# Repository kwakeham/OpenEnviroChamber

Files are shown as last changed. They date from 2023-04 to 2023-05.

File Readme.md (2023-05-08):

# Parts
- Arduino Leonardo (Uno or similar should work)
- Heater Power Fet: PSMN1R1-30PL (1.3mohm) or similar
- Fan Power Fet: P16NF06L or similar
- Heatsinks: Ohmite EV-T220-38E This mounts
- 2x XT60 connector pairs
- 2x "JST" 2 pin (I know JST is a brand but that's how they come up on Aliexpress or Jungle site)
- Adafruit MAX31855 Breadout Board (or similar but the mount won't line up)
- 2 x Bar magnets that fit in a 59 x 10mm trench (I think they were imperial)

- Top and Enclosure 3d printed
- M3 Inserts for the arduino mount
- 2 x 2mm self tapping screws for the MAX31855
- 12v Powersupply (min 5 amps)
- 50W PTC heater with fan (Jungle site)
- SSR for the compressor

- Thick Silicone wire for the 12v, enough to handle 5A but more for safety

# schematic
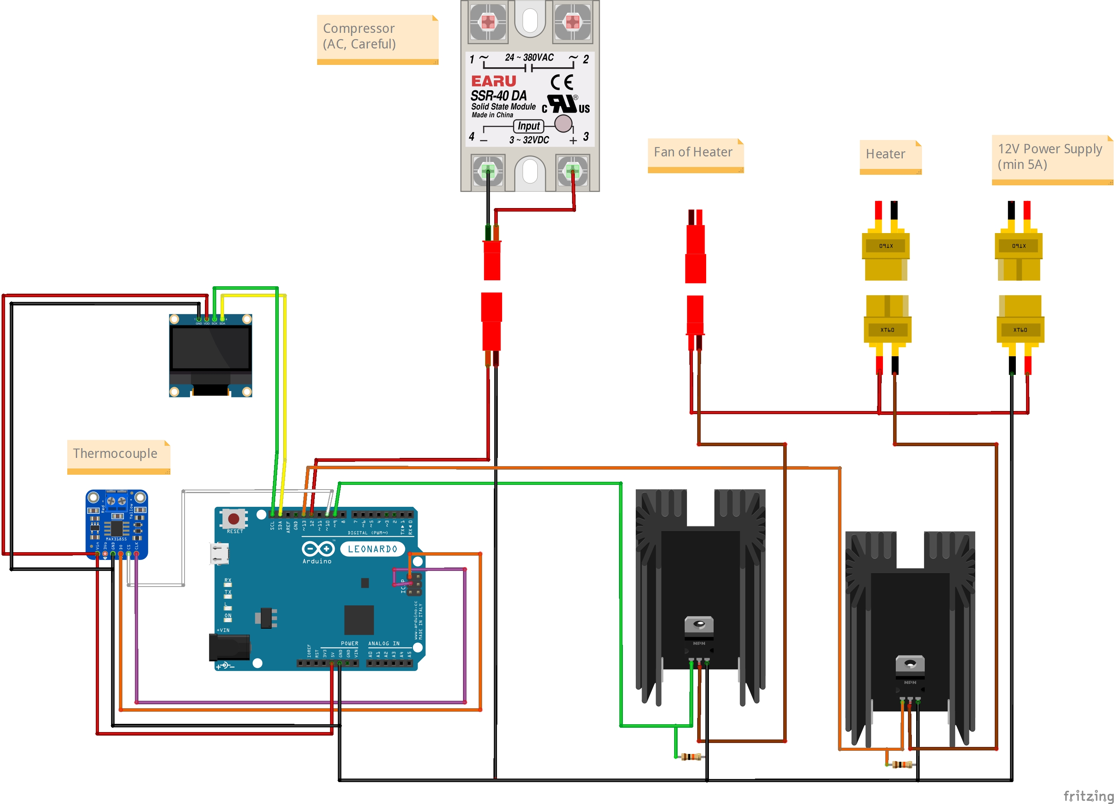
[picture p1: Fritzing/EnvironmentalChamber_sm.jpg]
Image of schematic


# Notes
I soldered wires to the back of the Arduino and modules because the push wires tend to be unreliable. I can't have a device that uses high power 12v and 120v AC going on the fritz. I suggest you do the same. Means debuging is easier

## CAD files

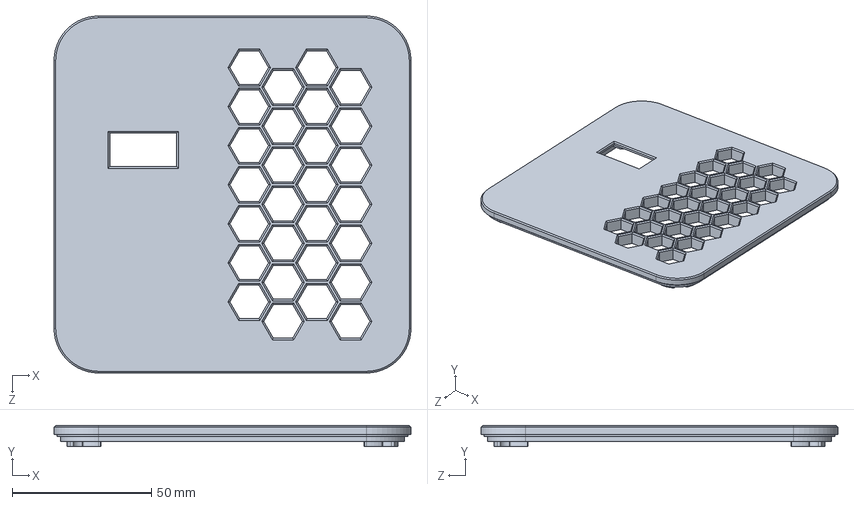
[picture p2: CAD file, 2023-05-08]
enclosure/Top.STEP
128.0 x 7.60 x 128.0 mm

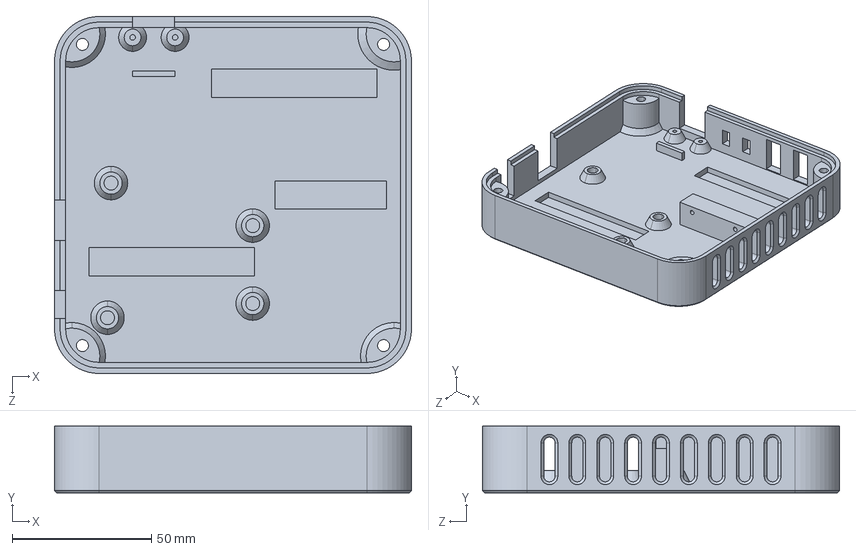
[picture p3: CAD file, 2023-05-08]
enclosure/Enclosure.STEP
128.0 x 24.0 x 128.0 mm

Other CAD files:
enclosure/Enclosure.3MF
enclosure/Top.3MF

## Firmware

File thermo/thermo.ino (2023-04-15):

/*
Frigidbear
*/

#include <SPI.h>
#include "Adafruit_MAX31855.h"
#include <Wire.h>
#include "SSD1306Ascii.h"
#include "SSD1306AsciiWire.h"
#include "ArduPID.h"
#include "Vrekrer_scpi_parser.h"

#define compressor_rest_time 300000 //5 minutes
#define cool_loop_time 30000 //30 seconds, we want the cooling loop time to be slower because compressors respond slowly

#define compressor_pin 12
#define heater_pin 13
#define fan_pin 9

// #define SCREEN_WIDTH 128 // OLED display width, in pixels
// #define SCREEN_HEIGHT 64 // OLED display height, in pixels
// // Declaration for an SSD1306 display connected to I2C (SDA, SCL pins)
// #define OLED_RESET     4 // Reset pin # (or -1 if sharing Arduino reset pin)
// Adafruit_SSD1306 display(SCREEN_WIDTH, SCREEN_HEIGHT, &Wire, OLED_RESET);

// 0X3C+SA0 - 0x3C or 0x3D
#define I2C_ADDRESS 0x3C
// Define proper RST_PIN if required.
#define RST_PIN -1
SSD1306AsciiWire oled;

#define MAXCS   10
Adafruit_MAX31855 thermocouple(MAXCS);

enum chamber_state_t {
  unknown_state,
  idle_state,
  cooling_state,
  heating_state
};

bool system_running = false;
bool compressor_state = false;
chamber_state_t chamber_state = idle_state;
double chamber_temp;
unsigned long compressor_stop_time = 0;

//ardupid
double heat_output;
double cool_output;
// Arbitrary setpoint and gains - adjust these as fit for your project:
double setpoint = 0;
double p_h = 30;
double i_h = 0.0002; //much lower I term
double d_h = 0;

double p_c = 11; //1 degree (gain of 10) should be good, but rounding and such so 11 it is
double i_c = 0.0002; //some i term for cooling
double d_c = 0;

//two controllers because we might end up tuning differently
ArduPID heatController;
ArduPID coolController;

SCPI_Parser my_instrument;

void setup() {

  Serial.begin(115200);
  while (!Serial) delay(1); // wait for Serial on Leonardo/Zero, etc

  Wire.begin();
  Wire.setClock(400000L);

#if RST_PIN >= 0
  oled.begin(&Adafruit128x64, I2C_ADDRESS, RST_PIN);
#else // RST_PIN >= 0
  oled.begin(&Adafruit128x64, I2C_ADDRESS);
#endif // RST_PIN >= 0

  oled.setFont(Adafruit5x7);
  oled.clear();

  //ensure the MAX31855 responds
  Serial.println("MAX31855 test");
  delay(200);  // wait for MAX chip to stabilize

  Serial.print("Initializing sensor...");
  if (!thermocouple.begin()) {
    Serial.println("ERROR.");
    while (1) delay(10);
  }
  Serial.println("MAX31855 startup DONE.");

  //set the SSR and Mosfet pin output
  pinMode(compressor_pin, OUTPUT);
  pinMode(heater_pin, OUTPUT);
  pinMode(fan_pin, OUTPUT);
  digitalWrite(fan_pin, true); //fan always on for now
  compressor_run(0); //This should be okay as it shouldn't update the compressor_state (initialize to false) and therefore compressor_stop_time should still be 0 for edge case on statup
  heater_control(0);

  //setup the two controllers.
  heatController.begin(&chamber_temp, &heat_output, &setpoint, p_h, i_h, d_h);
  heatController.setOutputLimits(0, 255);
  heatController.setWindUpLimits(0, 100); // Growth bounds for the integral term to prevent integral wind-up
  heatController.stop();                // Turn off the PID controller (compute() will not do anything until start() is called)
    
  coolController.begin(&chamber_temp, &cool_output, &setpoint, p_c, i_c, d_c);
  coolController.setOutputLimits(-255, 100); //allow some heat, but not much because we won't update quickly and don't want to fight compressor with heater
  coolController.setWindUpLimits(-20, 0); // limit cooling antiwindup but no heating integral
  coolController.setSampleTime(cool_loop_time);      // Slow time, but not too slow, compressor protection code should ensure no damage to compressor

  //scpi setup
  statusupdate("Waiting", system_running);
  oled.setCursor(0,1);
  oled.print("Stopped");

  my_instrument.RegisterCommand(F("*IDN?"), &Identify);
  my_instrument.SetCommandTreeBase(F("ENVI"));
    my_instrument.RegisterCommand(F(":SETTemperature"), &SetTemperature);
    my_instrument.RegisterCommand(F(":GETSettemperature?"), &GetSetTemperature);
    my_instrument.RegisterCommand(F(":TEMPerature?"), &GetTemperature);
    my_instrument.RegisterCommand(F(":COOL"), &ChamberMode);
    my_instrument.RegisterCommand(F(":HEAT"), &ChamberMode);
    my_instrument.RegisterCommand(F(":STAT?"), &ChamberState);
    my_instrument.RegisterCommand(F(":RUN"), &ChamberRun);
    my_instrument.RegisterCommand(F(":RUN?"), &isChamberRun);
    my_instrument.RegisterCommand(F(":STOP"), &ChamberStop);
    
  my_instrument.PrintDebugInfo(Serial);
}


void loop(void) {
  readtemp();
  my_instrument.ProcessInput(Serial, "\n");
  temperature_control();
  // display.display();
  delay(500);
  
}


//General system control
void temperature_control(void)
{
  if(system_running)
  {
    switch (chamber_state) {
      case unknown_state:
        break;
      case idle_state:
        break;
      case cooling_state:
        coolController.compute();
        compressor_control(cool_output);
        coolController.debug(&Serial, "cc", PRINT_INPUT    | // Can include or comment out any of these terms to print
                                              PRINT_OUTPUT   | // in the Serial plotter
                                              PRINT_SETPOINT |
                                              PRINT_BIAS     |
                                              PRINT_P        |
                                              PRINT_I        |
                                              PRINT_D);
        break;
      case heating_state:
        heatController.compute();
        heater_control(heat_output);
        compressor_run(false); //ensure off
        heatController.debug(&Serial, "hc", PRINT_INPUT    | // Can include or comment out any of these terms to print
                                              PRINT_OUTPUT   | // in the Serial plotter
                                              PRINT_SETPOINT |
                                              PRINT_BIAS     |
                                              PRINT_P        |
                                              PRINT_I        |
                                              PRINT_D);
        break;
      default:
        break;
    }
  }
  else //if not running make sure to shut off compressor
  {
    compressor_control(false);
    heater_control(0);
  }
}

void compressor_control(double coolvalue)
{
  if(coolvalue < -10)
  {
    compressor_run(true);
  }
  else
  {
    compressor_run(false);
  }
  if (coolvalue > 0)
  {
    heater_control(coolvalue);
  } else
  {
    heater_control(0); //ensure off
  }

}
//guards the compressor
void compressor_run(bool compressor_run)
{
  //true if we want compressor to run
  if (compressor_run)
  {  
    //edge case of startup
    if(compressor_stop_time == 0)
    {
      compressor_state = true;
      digitalWrite(compressor_pin, true);
    }
    else if (millis() > (compressor_stop_time + compressor_rest_time))
    {
      compressor_state = true;
      digitalWrite(compressor_pin, true);
    }
    // If it wasn't a startup condition and it hasn't been enought time  to reset the compressor(compressor_rest_time) stay off
    else
    {
      digitalWrite(compressor_pin, false); // I don't think we need this but just in case
    }
  }
  //commanded not to run
  else
  {
    // If the compressor was running and we're now commanded to shut it off
    // Now we shouldn't be able to store the compressor state until it was on
    if (compressor_state)
    {
      compressor_state = false; //remember the state
      compressor_stop_time = millis();  //remember the time we shut it off
      Serial.print("Stop time: "); //a little debug
      Serial.println(compressor_stop_time);
    }
    //always allow shutdown of the compressor
    digitalWrite(compressor_pin, false);
  }  
}

void heater_control(double heatvalue)
{
  analogWrite(heater_pin, heatvalue); //ensure heater is off
}


//MAX31855 Thermocouple
void readtemp(void)
{
  double temporary_temperature = thermocouple.readCelsius();
  if (isnan(temporary_temperature)) {
     Serial.println("Something wrong with thermocouple!");
  }
  else
  {
    chamber_temp = temporary_temperature;
    oled.setCursor(90,2);
    oled.print(chamber_temp);
    oled.print("c");
  }
}


//OLED
void statusupdate(String currentstatus, bool runningstatus)
{
  oled.clear();
  oled.print(currentstatus);
}

//SCPI

void Identify(SCPI_C commands, SCPI_P parameters, Stream& interface) {
  interface.println(F("Vrekrer,SCPI Dimmer,#00," VREKRER_SCPI_VERSION));
  //*IDN? Suggested return string should be in the following format:
  // "<vendor>,<model>,<serial number>,<firmware>"
}

void SetTemperature(SCPI_C commands, SCPI_P parameters, Stream& interface) {
  // For simplicity no bad parameter check is done.
  if (parameters.Size() > 0) {
    setpoint = constrain(String(parameters[0]).toInt(), 0, 255);
  }
}

void GetTemperature(SCPI_C commands, SCPI_P parameters, Stream& interface) {
  interface.print(":GETTemperature: ");
  interface.println(String(chamber_temp, DEC));
}

void GetSetTemperature(SCPI_C commands, SCPI_P parameters, Stream& interface) {
  interface.print(":GETSettemperature: ");
  interface.println(String(setpoint, DEC));
}

void ChamberMode(SCPI_C commands, SCPI_P parameters, Stream& interface) {
  String last_header = String(commands.Last());
  last_header.toUpperCase();
  if (last_header.startsWith("HEAT")) {
    chamber_state = heating_state;
    heatController.start();
    coolController.stop();
    oled.setCursor(0,0);
    oled.print("Heating");
  } else {
    chamber_state = cooling_state;
    heatController.stop();
    coolController.start();
    oled.setCursor(0,0);
    oled.print("Cooling");
  }
}
void ChamberState(SCPI_C commands, SCPI_P parameters, Stream& interface) {
  if (chamber_state == heating_state)
  {
    interface.println(":heating_state");
  } else if (chamber_state == cooling_state)
  { 
    interface.println(":cooling_state");
  }
}

void ChamberRun(SCPI_C commands, SCPI_P parameters, Stream& interface) {
  system_running = true; 
  heatController.reset();//reset the I and D terms for heat controller
  coolController.reset(); //reset the I and D terms for the cooling controller, though it's unlikely we have I and D
  oled.setCursor(0,1);
  oled.print("Running");

}

void ChamberStop(SCPI_C commands, SCPI_P parameters, Stream& interface) {
  system_running = false;
  oled.setCursor(0,1);
  oled.print("Stopped");
}

void isChamberRun(SCPI_C commands, SCPI_P parameters, Stream& interface) {
  if (system_running)
  {
    interface.println("Chamber Running");
  } else
  { 
    interface.println("Chamber NOT Running");
  }
}

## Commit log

2023-03-17 get and set temperature, return chamber temp
2023-03-17 add heating and cooling commands
2023-03-17 heating state running
2023-03-17 remove some debug and add comments to heater_control
2023-03-18 seperate heating and cooling gains, fix compressor control
2023-03-18 reduced heating intergral and reset controllers on run
2023-03-19 reduce integral for heat, added it to cool
2023-04-13 added fan pin control
2023-05-08 adding stuff related to how to build and enclosures
    [Enclosure.3MF, Enclosure.STEP, EnvironmentalChamber.fzz, Top.3MF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]
